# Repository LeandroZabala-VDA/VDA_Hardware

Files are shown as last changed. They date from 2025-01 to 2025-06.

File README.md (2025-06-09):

# VDA_Hardware

This repository contains the hardware design files for the **VDA Signal Acquisition System**, a device developed for the non-invasive measurement of **Arterial Diameter Variation (VDA)** using piezoelectric transducers. The system is intended for biomedical research applications and has been validated in both laboratory and clinical environments.

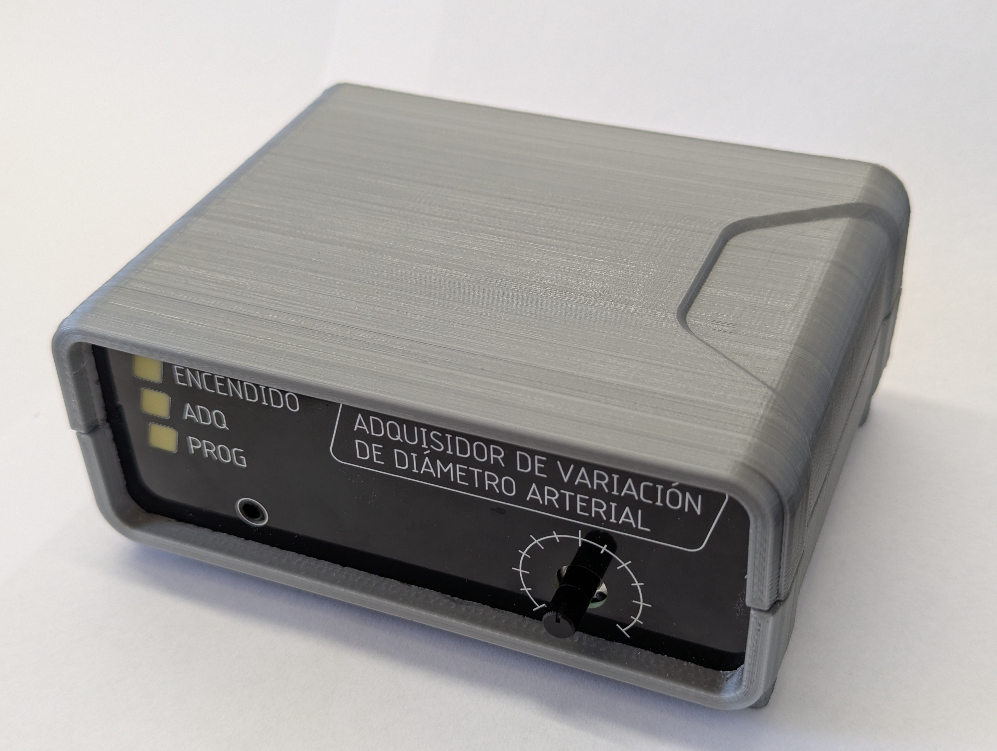
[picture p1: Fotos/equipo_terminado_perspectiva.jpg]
Equipo terminadp


## 📁 Repository Structure

- **/Adquisidor**  
  Contains all design files for the main acquisition board, including schematics, PCB layout, and bill of materials. This board handles signal conditioning, high-resolution analog-to-digital conversion, power regulation, and communication with the PC interface.

- **/frente del gabinete**  
  Includes the PCB designs used as front and rear panels for the device enclosure. These boards support mechanical mounting of connectors, status indicators, and user controls.

## 🛠️ Tools and Compatibility

- Designed using **Autodesk Eagle**  
- Compatible with Eagle version 9.6.2 or later

## ✅ Hardware Status

The version published here is fully functional and has been used in real experimental protocols and patient measurements. It is part of a broader open-source platform that includes firmware and a Python-based user interface.

Key features include:
- Support for a 27 mm piezoelectric transducer
- Fully differential charge amplifier
- Analog bandwidth: 0.16 Hz – 34 Hz
- 16-bit sigma-delta ADC
- 50 Hz digital notch filter
- Electrically isolated sensor interface

## 📂 Included Files

- `.sch` and `.brd` files (schematics and board layout)
- Bill of Materials (`.xls` / `.csv`)
- Reference images of the PCB and assembly
- Enclosure drawings or panel layouts (`.png`, `.step`, etc.)

## 📷 Preview

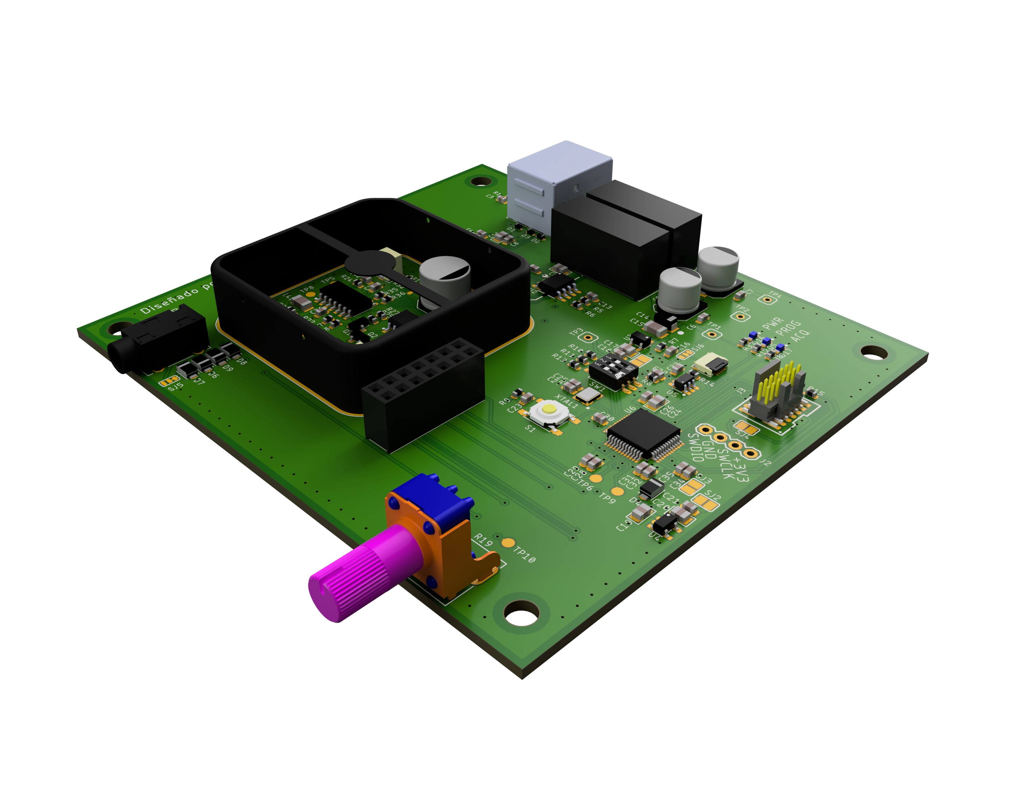
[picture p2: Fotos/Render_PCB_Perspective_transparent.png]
Render PCB


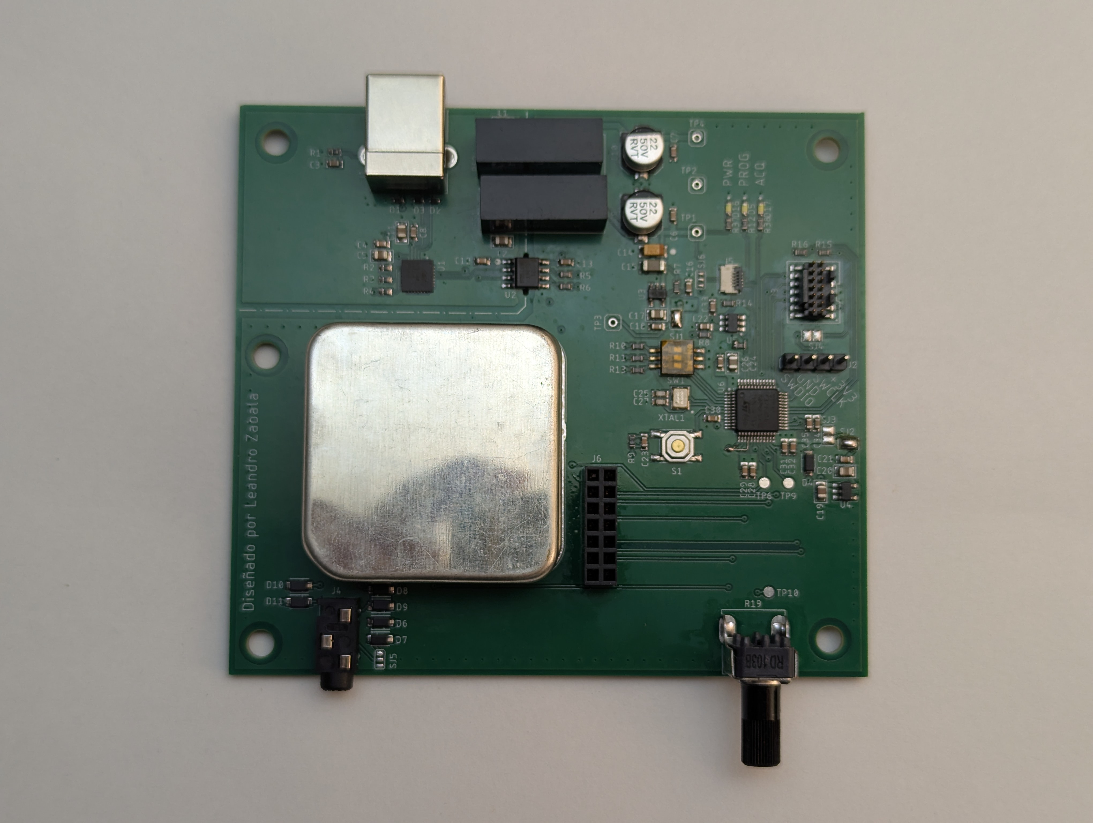
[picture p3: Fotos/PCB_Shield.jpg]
Real PCB


## 🧩 Related Work

This hardware was developed as part of a final project at the **Laboratorio de Bioingeniería (LABI)**, Universidad Nacional de Mar del Plata (Argentina), and was used in the context of scientific publications, including a peer-reviewed IEEE article.

## 🛡 License

All hardware design files in this repository are licensed under the **CERN Open Hardware License v2 - Strongly Reciprocal (CERN-OHL-S)**.

Any derivative work must also remain open and be shared under the same terms. 

## 📬 Contact

For questions, suggestions or collaboration, feel free to open an issue or contact me.

leandrozabala@mdp.edu.ar

---

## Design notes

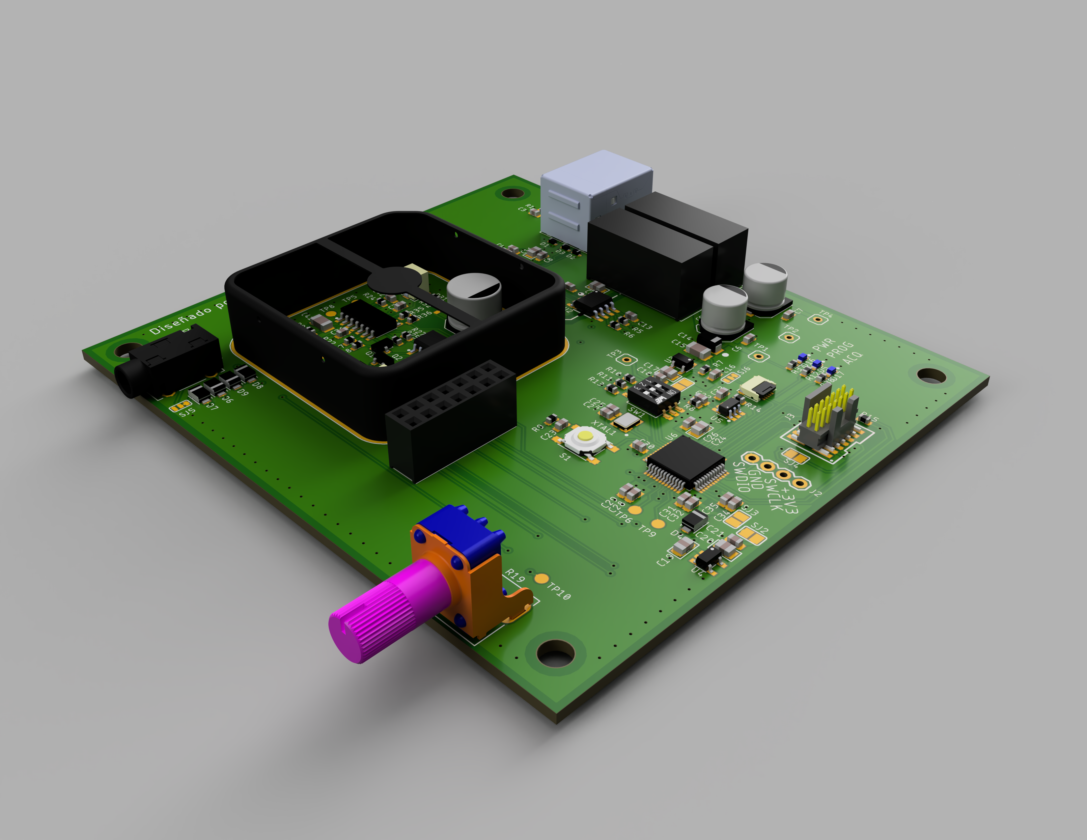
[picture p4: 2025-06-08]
Fotos/Render_PCB_Perspective_gray.png

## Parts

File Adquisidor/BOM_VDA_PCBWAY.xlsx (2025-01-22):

Item # | Parts | Qty | MPN | Description | Package | Instruction | LINK
1 | R5, R6, R15, R16, R29, R33,R20, R21 | 8 | RC0603FR-07100RL |  | R_0603 |  | https://www.lcsc.com/product-detail/Chip-Resistor-Surface-Mount_YAGEO-RC0603FR-07100RL_C105588.html
2 | R7, R24 | 2 | RC0603FR-07100KL |  | R_0603 |  | https://www.lcsc.com/product-detail/Chip-Resistor-Surface-Mount_YAGEO-RC0603FR-07100KL_C14675.html
3 | R22, R23 | 2 | CRCW060310M0DHEAP |  | R_0603 |  | https://www.lcsc.com/product-detail/Chip-Resistor-Surface-Mount_Vishay-Intertech-CRCW060310M0DHEAP_C4098828.html
4 | R8, R9, R10, R11, R13, R14 | 6 | RC0603FR-0710KL |  | R_0603 |  | https://www.lcsc.com/product-detail/Chip-Resistor-Surface-Mount_YAGEO-RC0603FR-0710KL_C98220.html
5 | R26 | 1 | RC0603FR-07150RL |  | R_0603 |  | https://www.lcsc.com/product-detail/Chip-Resistor-Surface-Mount_YAGEO-RC0603FR-07150RL_C114608.html
6 | R18 | 1 | RC0603FR-0733KL |  | R_0603 |  | https://www.lcsc.com/product-detail/Chip-Resistor-Surface-Mount_YAGEO-RC0603FR-0733KL_C126359.html
7 | R25, R28, R31, R35 | 4 | RC0603FR-071KL |  | R_0603 |  | https://www.lcsc.com/product-detail/Chip-Resistor-Surface-Mount_YAGEO-RC0603FR-071KL_C22548.html
8 | R36 | 1 | RC0603FR-072K2L |  | R_0603 |  | https://www.lcsc.com/product-detail/Chip-Resistor-Surface-Mount_YAGEO-RC0603FR-072K2L_C114662.html
9 | R12, R37, R38 | 3 | RC0603FR-07270RL |  | R_0603 |  | https://www.lcsc.com/product-detail/Chip-Resistor-Surface-Mount_YAGEO-RC0603FR-07270RL_C137754.html
10 | R27 | 1 | RC0603FR-072KL |  | R_0603 |  | https://www.lcsc.com/product-detail/Chip-Resistor-Surface-Mount_YAGEO-RC0603FR-072KL_C105576.html
11 | R4 | 1 | RC0402FR-071KL |  | R0402 |  | https://www.lcsc.com/product-detail/Chip-Resistor-Surface-Mount_YAGEO-RC0402FR-071KL_C106235.html
12 | R2 | 1 | RC0402FR-0722K1L |  | R0402 |  | https://lcsc.com/product-detail/Chip-Resistor-Surface-Mount_YAGEO-RC0402FR-0722K1L_C163478.html
13 | R1, R3 | 2 | RC0402FR-0747K5L |  | R0402 |  | https://lcsc.com/product-detail/Chip-Resistor-Surface-Mount_YAGEO-RC0402FR-0747K5L_C137974.html
14 | R30, R32 | 2 | 3224W-1-501E |  | RV3.2X4 |  | https://www.lcsc.com/product-detail/Potentiometers-Variable-Resistors_BOURNS-3224W-1-501E_C116324.html?s_z=n_3224W
15 | R19 | 1 | RK09K1110077 |  | POT-09VR1M |  | https://www.lcsc.com/product-detail/Potentiometers-Variable-Resistors_ALPSALPINE-RK09K1110077_C3020620.html?s_z=n_RK09K1110077
16 | R17, R34 | 2 | DNP |  | R_0603
17 | C3, C4, C6, C7, C8, C12, C13, C23, C26, C28, C29, C30, C31, C32, C33, C36, C37, C38, C39,C18, C21, C35 | 22 | C0603C104K5RACAUTO |  | C_0603 |  | https://lcsc.com/product-detail/Multilayer-Ceramic-Capacitors-MLCC-SMD-SMT_KEMET-C0603C104K5RACAUTO_C129621.html
18 | C40, C41 | 2 | GRM31C5C1H104FA01L | NP0 | C_1206 |  | https://www.lcsc.com/product-detail/Multilayer-Ceramic-Capacitors-MLCC-SMD-SMT_Murata-Electronics-GRM31C5C1H104FA01L_C2981728.html?s_z=n_C0G
19 | C25, C27 | 2 | CC0603JRNPO9BN100 |  | C_0603 |  | https://www.lcsc.com/product-detail/Multilayer-Ceramic-Capacitors-MLCC-SMD-SMT_YAGEO-CC0603JRNPO9BN100_C106245.html
20 | C16, C22 | 2 | CL10B224KA8NNNC |  | C_0603 |  | https://www.lcsc.com/product-detail/Multilayer-Ceramic-Capacitors-MLCC-SMD-SMT_Samsung-Electro-Mechanics-CL10B224KA8NNNC_C21120.html
21 | C42 | 1 | CC0603JRX7R9BB473 |  | C_0603 |  | https://www.lcsc.com/product-detail/Multilayer-Ceramic-Capacitors-MLCC-SMD-SMT_YAGEO-CC0603JRX7R9BB473_C519554.html
22 | C34 | 1 | CL10A105KO8NNNC |  | C_0603 |  | https://lcsc.com/product-detail/Multilayer-Ceramic-Capacitors-MLCC-SMD-SMT_Samsung-Electro-Mechanics-CL10A105KO8NNNC_C1592.html
23 | C5, C11,C24,C1, C2, C17, C20 | 7 | CL21A475KAQNNNE |  | C_0805 |  | https://www.lcsc.com/product-detail/Multilayer-Ceramic-Capacitors-MLCC-SMD-SMT_Samsung-Electro-Mechanics-CL21A475KAQNNNE_C1779.html
24 | C19 | 1 | CL21A106KAYNNNE |  | C_0805 |  | https://www.lcsc.com/product-detail/Multilayer-Ceramic-Capacitors-MLCC-SMD-SMT_Samsung-Electro-Mechanics-CL21A106KAYNNNE_C15850.html
25 | C15 | 1 | HGC1206R5476M250NSPJ |  | C_1206 |  | https://www.lcsc.com/product-detail/Multilayer-Ceramic-Capacitors-MLCC-SMD-SMT_Chinocera-HGC1206R5476M250NSPJ_C22367835.html
26 | C14 | 1 | TAJA476K006RNJ |  | A_3216 |  | https://lcsc.com/product-detail/Tantalum-Capacitors_Kyocera-AVX-TAJA476K006RNJ_C7190.html
27 | C9, C10 | 2 | RVT1H220M0605 |  | CAPAE660X590N |  | https://www.lcsc.com/product-detail/Aluminum-Electrolytic-Capacitors-SMD_ROQANG-RVT1H220M0605_C72505.html
28 | C43 | 1 |  |  | CAPAE830X680N
29 | D1, D2, D3 | 3 | LESD5D5.0CT1G |  | SOD523 |  | https://www.lcsc.com/product-detail/span-style-background-color-ff0-ESD-span-and-Surge-Protection-TVS-span-style-background-color-ff0-ESD-span_UMW-Youtai-Semi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
30 | D4 | 1 | LMBR140T1G |  | SOD123W |  | https://www.lcsc.com/product-detail/Schottky-Diodes_LRC-LMBR140T1G_C81142.html
31 | D16, D5, D17 | 3 | XL-1608UWC-04 |  | LED_0603_ARROW |  | https://www.lcsc.com/product-detail/LED-Indication-Discrete_XINGLIGHT-XL-1608UWC-04_C965808.html
32 | D6, D7, D8, D9, D10, D11, D12, D13, D14, D15 | 10 | 1N4148W |  | SOD123W |  | https://www.lcsc.com/product-detail/Switching-Diode_Jiangsu-Changjing-Electronics-Technology-Co-Ltd-1N4148W_C2099.html
33 | U1 | 1 | CP2102N-A02-GQFN28R |  | MLP28 |  | https://lcsc.com/product-detail/USB-ICs_SILICON-LABS-CP2102N-A02-GQFN28R_C964632.html
34 | U2 | 1 | ISO7721DR |  | SO8 |  | https://www.lcsc.com/product-detail/Digital-Isolators_Texas-Instruments-ISO7721DR_C366164.html?s_z=n_ISO7721DR
35 | U3, U4 | 2 | LP5907MFX-3.3/NOPB |  | SOT23-5 |  | https://www.lcsc.com/product-detail/Voltage-Regulators-Linear-Low-Drop-Out-LDO-Regulators_Texas-Instruments-LP5907MFX-3-3-NOPB_C80670.html
36 | U5 | 1 | SN74LVC1G175DBVR |  | SOT-23-6 |  | https://www.lcsc.com/product-detail/Flip-Flops_Texas-Instruments-SN74LVC1G175DBVR_C128412.html?s_z=n_SN74LVC1G175
37 | U6 | 1 | STM32F373CBT6 |  | QFP50P900X900X160-48N |  | https://www.lcsc.com/product-detail/Microcontrollers-MCU-MPU-SOC_STMicroelectronics-STM32F373CBT6_C1337334.html
38 | U7 | 1 | TL074IDT |  | SOIC127P600X175-14N |  | https://www.lcsc.com/product-detail/FET-Input-Amplifiers_STMicroelectronics-TL074IDT_C107644.html?s_z=n_TL074
39 | U8 | 1 | LM13700M/NOPB |  | SO16 |  | https://www.lcsc.com/product-detail/Operational-Amplifier_Texas-Instruments-LM13700M-NOPB_C1346265.html?s_z=n_LM13700
40 | Q1, Q2 | 2 | BC856B,215 |  | SOT-23 |  | https://www.lcsc.com/product-detail/Bipolar-BJT_Nexperia-BC856B-215_C109310.html?s_z=n_BC856
41 | PS1, PS2 | 2 | IF0505S-2W |  | 0505S-2WR3 |  | https://www.lcsc.com/product-detail/Isolated-Power-Modules_YLPTEC-IF0505S-2W_C5369639.html?s_z=n_F0505S-2W
42 | SW1 | 1 | DSHP03TSGER |  | DIPSW-3 |  | https://www.lcsc.com/product-detail/DIP-Switches_kangshen-DSHP03TSGER_C3293143.html
43 | SHIELD1 | 1 | MS384-10F |  | MS384 | Only solder 2 pads. DO NOT SOLDER ALL THE WAY ARROUND TO THE GND PLANE | https://www.digikey.com/en/products/detail/masach-tech-ltd/MS384-10F/12084532
44 | SHIELD_COVER | 1 | MS384-10C |  |  | Placed on top of the shield | https://www.digikey.com/en/products/detail/masach-tech-ltd/MS384-10C/12084599
45 | S1 | 1 | TS-1187A-B-A-B |  | SMTR2 |  | https://www.lcsc.com/product-detail/Tactile-Switches_XKB-Connection-TS-1187A-B-A-B_C318884.html
46
47 | J1 | 1 | BF 90° |  | USB-B |  | https://www.lcsc.com/product-detail/USB-Connectors_SHOU-HAN-BF-90_C456014.html
48 | J2 | 1 | PZ254V-11-04P |  | 1X04 |  | https://www.lcsc.com/product-detail/Pin-Headers_XFCN-PZ254V-11-04P_C2691448.html
49 | J3 | 1 | FTSH-107-01-L-DV-K-A |  | SAMTEC_FTSH-107-01-L-DV-K-A |  | https://www.lcsc.com/product-detail/Pin-Headers_Samtec-FTSH-107-01-L-DV-K-A_C5563894.html?s_z=n_FTSH-107-01-L-DV-K-A
50 | J4 | 1 | PJ-3200 |  | PJ-3200 |  | https://www.lcsc.com/product-detail/Audio-Connectors_XKB-Connection-PJ-3200_C2689690.html?s_z=n_PJ-3200
51 | J5 | 1 | F0504-H-05-10G-R | FFC, FPC (Flat Flexible) Connector | F0504-H-05-10G-R |  | https://www.lcsc.com/product-detail/FFC-FPC-Flat-Flexible-Connector-Assemblies_XFCN-F0504-H-05-10G-R_C2889992.html?s_z=n_F0504-H-05-10G-R
52 | J6 | 1 | 2.54-2*7P |  | CONN-VERT-2.54MM-2X7-FEMALE |  | https://www.lcsc.com/product-detail/Female-Headers_BOOMELE-Boom-Precision-Elec-2-54-2-7P_C38844.html
53 | XTAL1 | 1 | S32080001010500 |  | XTAL3.2X2.5 |  | https://lcsc.com/product-detail/Crystals_JGHC-S32080001010500_C479191.html
54 | FLEX | 1 | JS05A-05P-120-4-8 |  | Flex 12cm 5P pitch=0.5mm | Connected to J5 | https://www.lcsc.com/product-detail/FFC-Cable-Flexible-Flat-Cable_JUSHUO-JS05A-05P-120-4-8_C5371200.html

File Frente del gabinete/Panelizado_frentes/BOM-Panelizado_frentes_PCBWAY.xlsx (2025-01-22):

Item # | Parts | Qty | MPN | Description | Package | Instruction | LINK
1 | R2, R5, R8 | 3 | RC0603FR-07100KL |  | R_0603 |  | https://www.lcsc.com/product-detail/Chip-Resistor-Surface-Mount_YAGEO-RC0603FR-07100KL_C14675.html
2 | R1, R3, R4, R6, R7, R9 | 6 | RC0603FR-07100RL |  | R_0603 |  | https://www.lcsc.com/product-detail/Chip-Resistor-Surface-Mount_YAGEO-RC0603FR-07100RL_C105588.html
3 | Q2, Q3, Q1 | 3 | BSS138 |  | SOT-23 |  | https://www.lcsc.com/product-detail/MOSFETs_MDD-Microdiode-Semiconductor-BSS138_C427380.html
4 | J1 | 1 | F0504-H-05-10G-R | FFC, FPC (Flat Flexible) Connector | F0504-H-05-10G-R |  | https://www.lcsc.com/product-detail/FFC-FPC-Flat-Flexible-Connector-Assemblies_XFCN-F0504-H-05-10G-R_C2889992.html?s_z=n_F0504-H-05
5 | D4, D5, D6 | 3 | VLRK31R1S2-GS08 |  | VLRK31 |  | https://www.lcsc.com/product-detail/LED-Indication-Discrete_Vishay-Intertech-VLRK31R1S2-GS08_C5346037.html?s_z=n_VLRK31
6 | FLEX | 1 | YTC05B-05P-220-3-4 | Connected to J1 | Flex 22cm 5P pitch=0.5mm | Connected to J1 | https://www.lcsc.com/product-detail/FFC-Cable-Flexible-Flat-Cable_YIYUAN-YTC05B-05P-220-3-4_C20069054.html

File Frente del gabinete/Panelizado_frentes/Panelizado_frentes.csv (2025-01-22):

Qty | Value | Device | Package | Parts | Description | MPN | LINK
3 | 100K | R_0603 | R_0603 | R2, R5, R8 |  | RC0603FR-07100KL | https://www.lcsc.com/product-detail/Chip-Resistor-Surface-Mount_YAGEO-RC0603FR-07100KL_C14675.html
6 | 100R | R_0603 | R_0603 | R1, R3, R4, R6, R7, R9 |  | RC0603FR-07100RL | https://www.lcsc.com/product-detail/Chip-Resistor-Surface-Mount_YAGEO-RC0603FR-07100RL_C105588.html
3 | BSS138 | N-MOS_SOT23-3 | SOT-23 | 2, 3, Q1 |  | BSS138 | https://www.lcsc.com/product-detail/MOSFETs_MDD-Microdiode-Semiconductor-BSS138_C427380.html
1 | F0504-H-05-10G-R | F0504-H-05-10G-R | F0504-H-05-10G-R | J1 | FFC, FPC (Flat Flexible) Connector | F0504-H-05-10G-R | https://www.lcsc.com/product-detail/FFC-FPC-Flat-Flexible-Connector-Assemblies_XFCN-F0504-H-05-10G-R_C2889992.html?s_z=n_F0504-H-05
3 | LED-REVERSE_MOUNT | LED-REVERSE_MOUNT | VLRK31 | D4, D5, D6 |  | VLRK31R1S2-GS08 | https://www.lcsc.com/product-detail/LED-Indication-Discrete_Vishay-Intertech-VLRK31R1S2-GS08_C5346037.html?s_z=n_VLRK31

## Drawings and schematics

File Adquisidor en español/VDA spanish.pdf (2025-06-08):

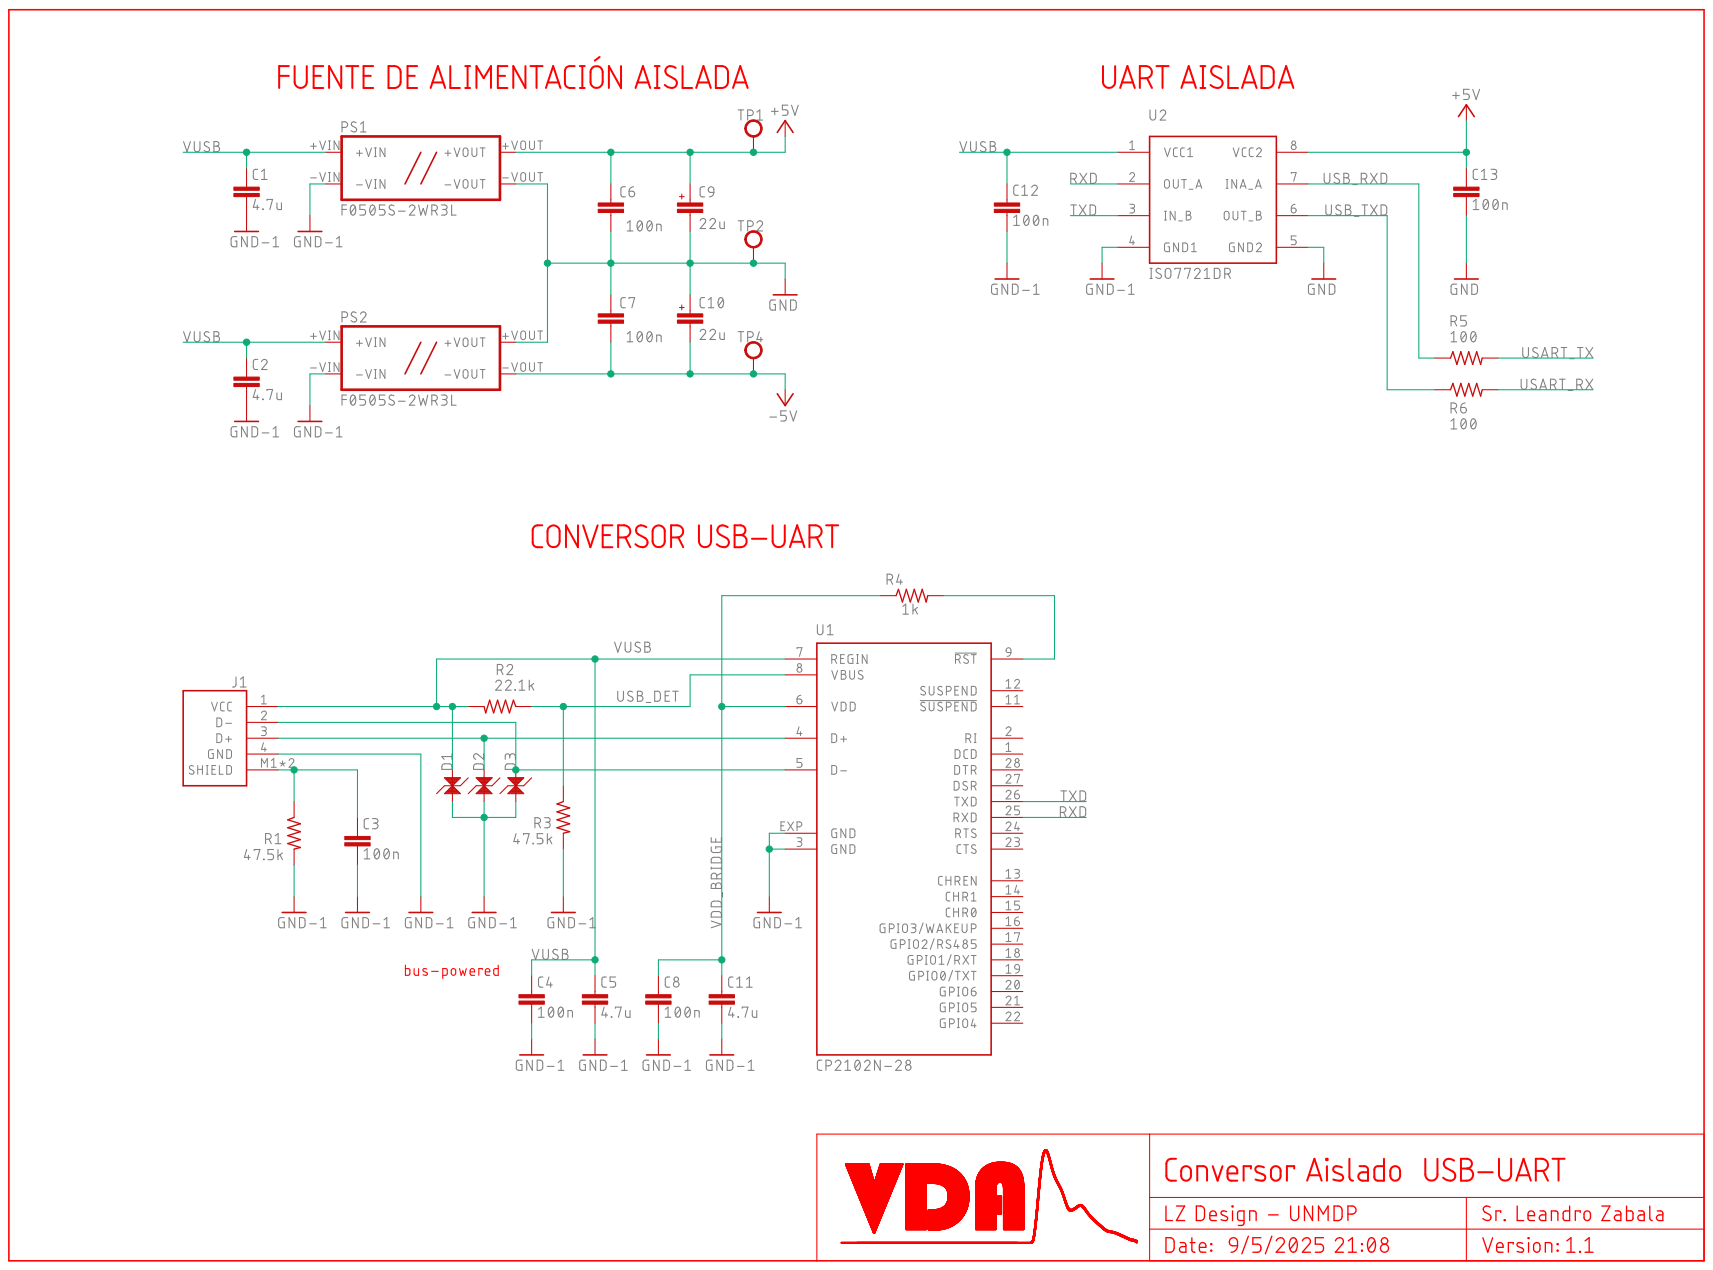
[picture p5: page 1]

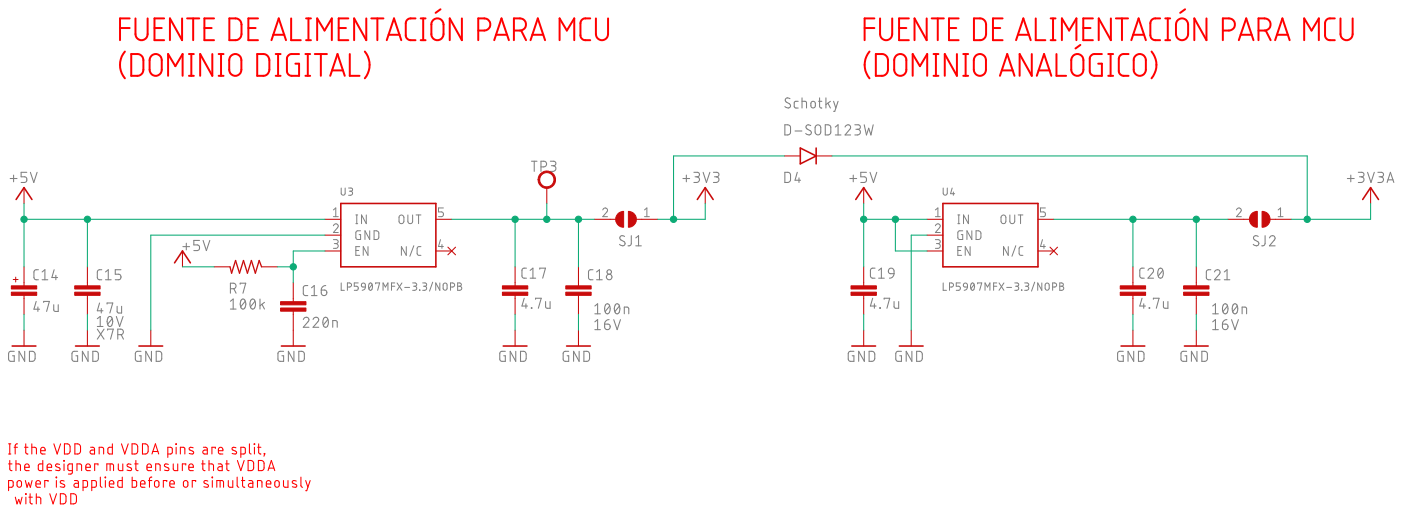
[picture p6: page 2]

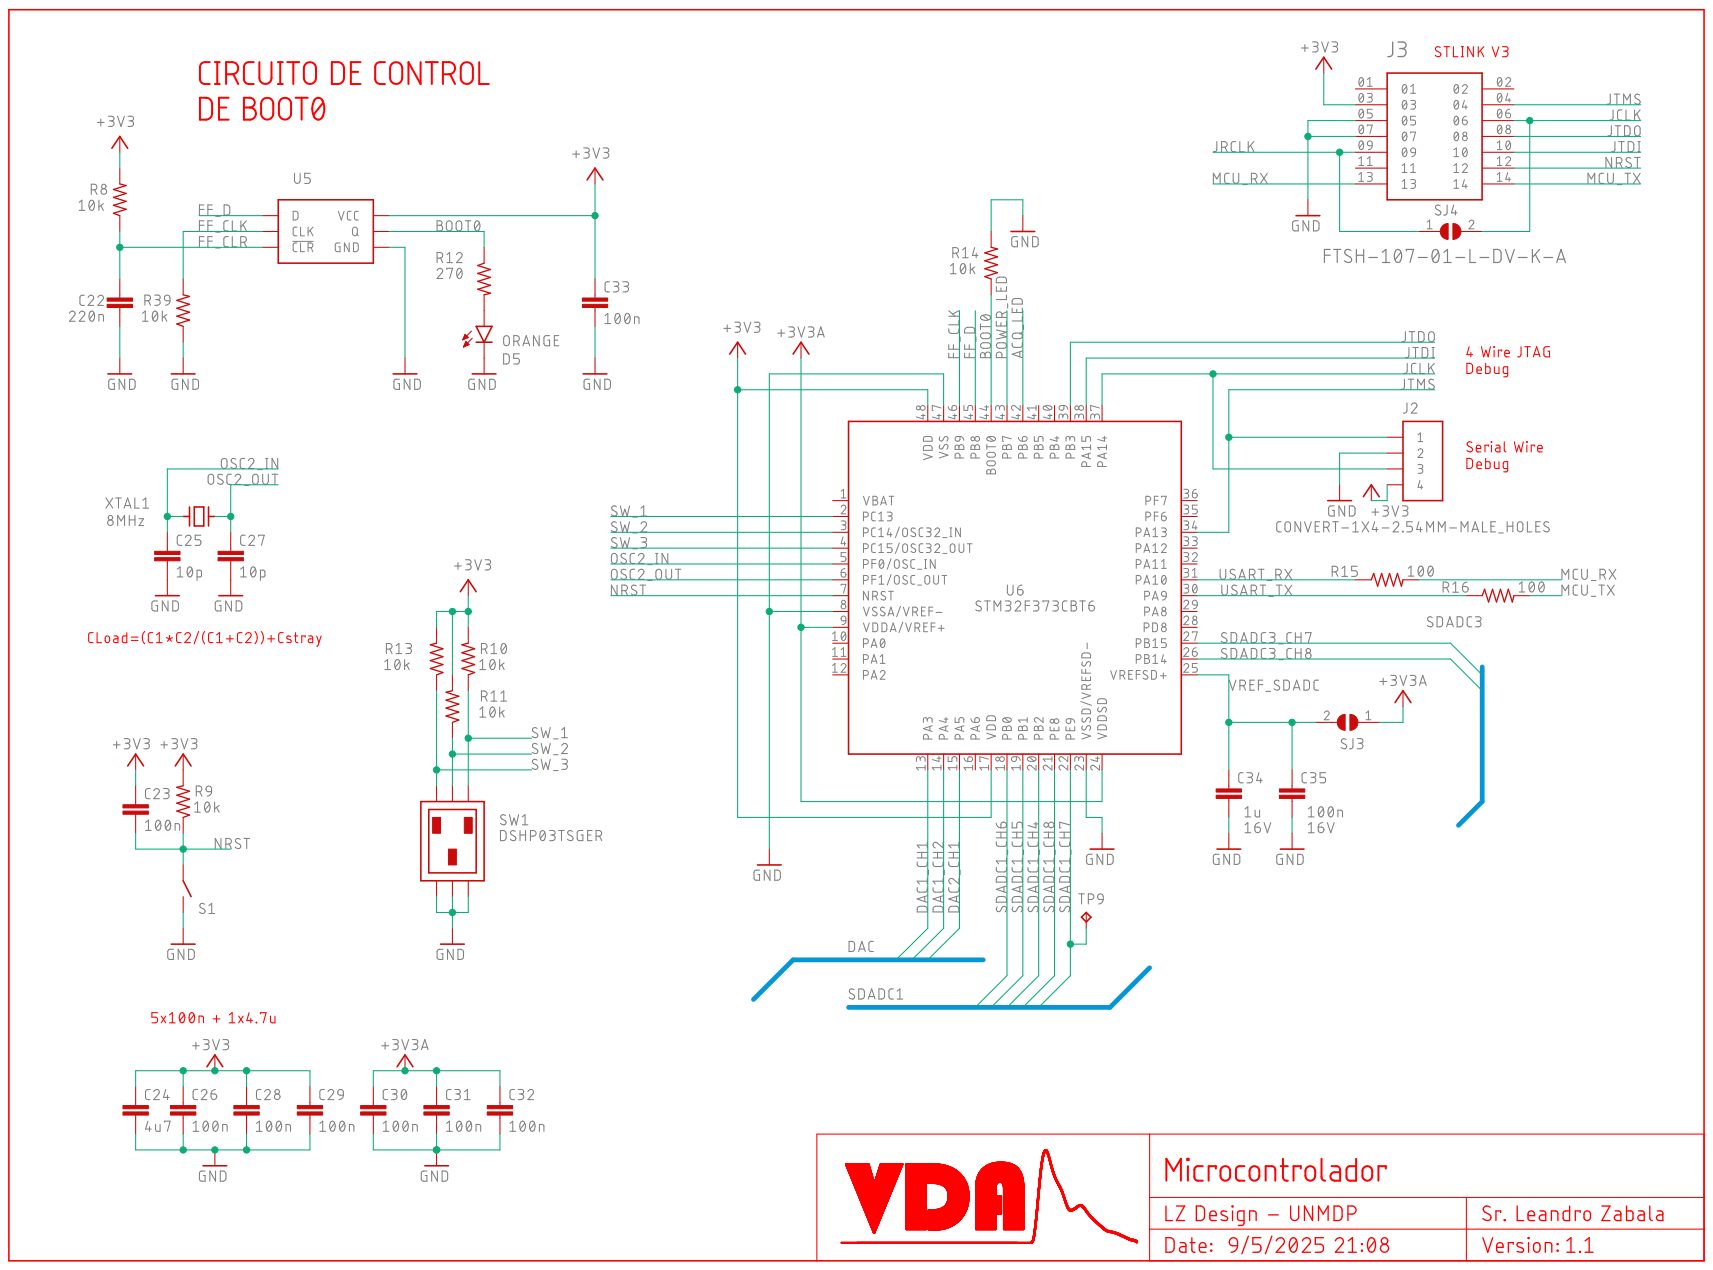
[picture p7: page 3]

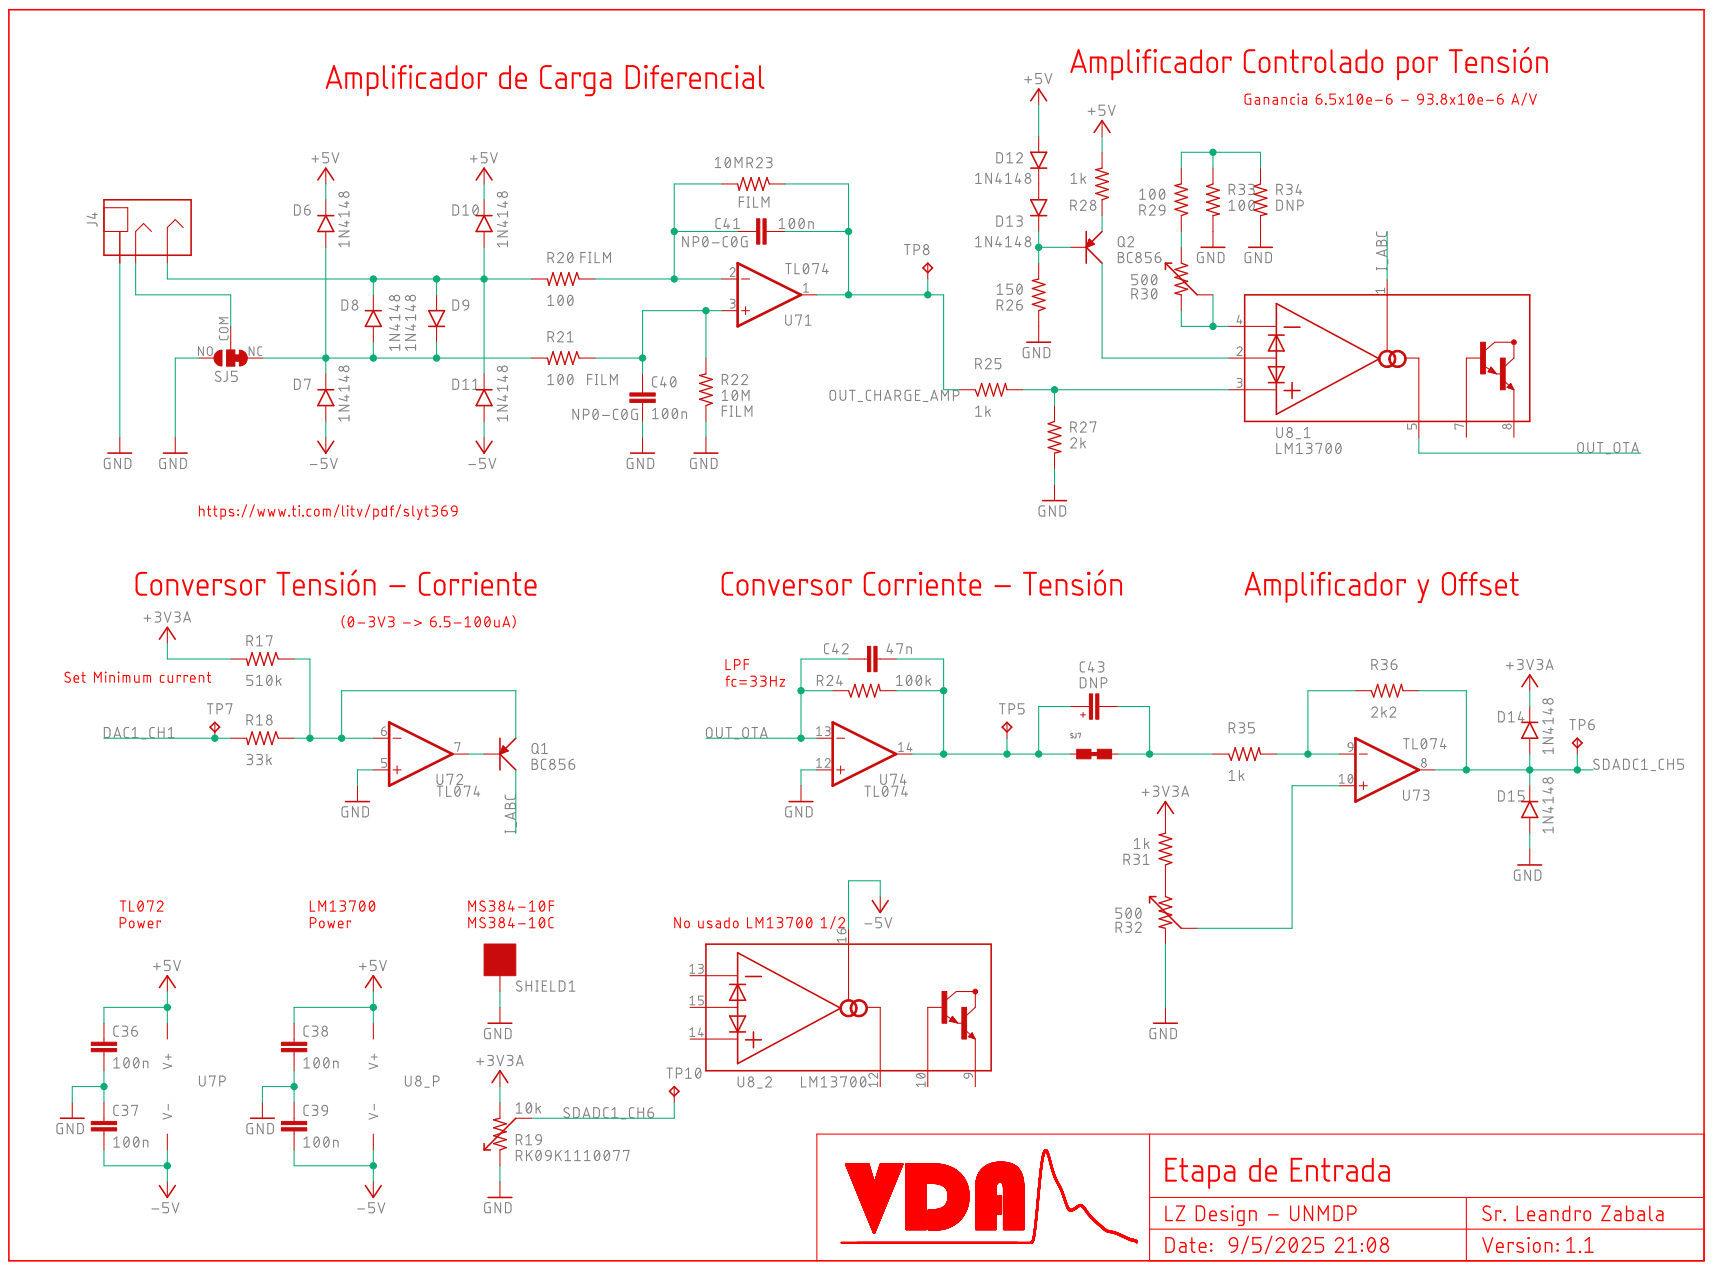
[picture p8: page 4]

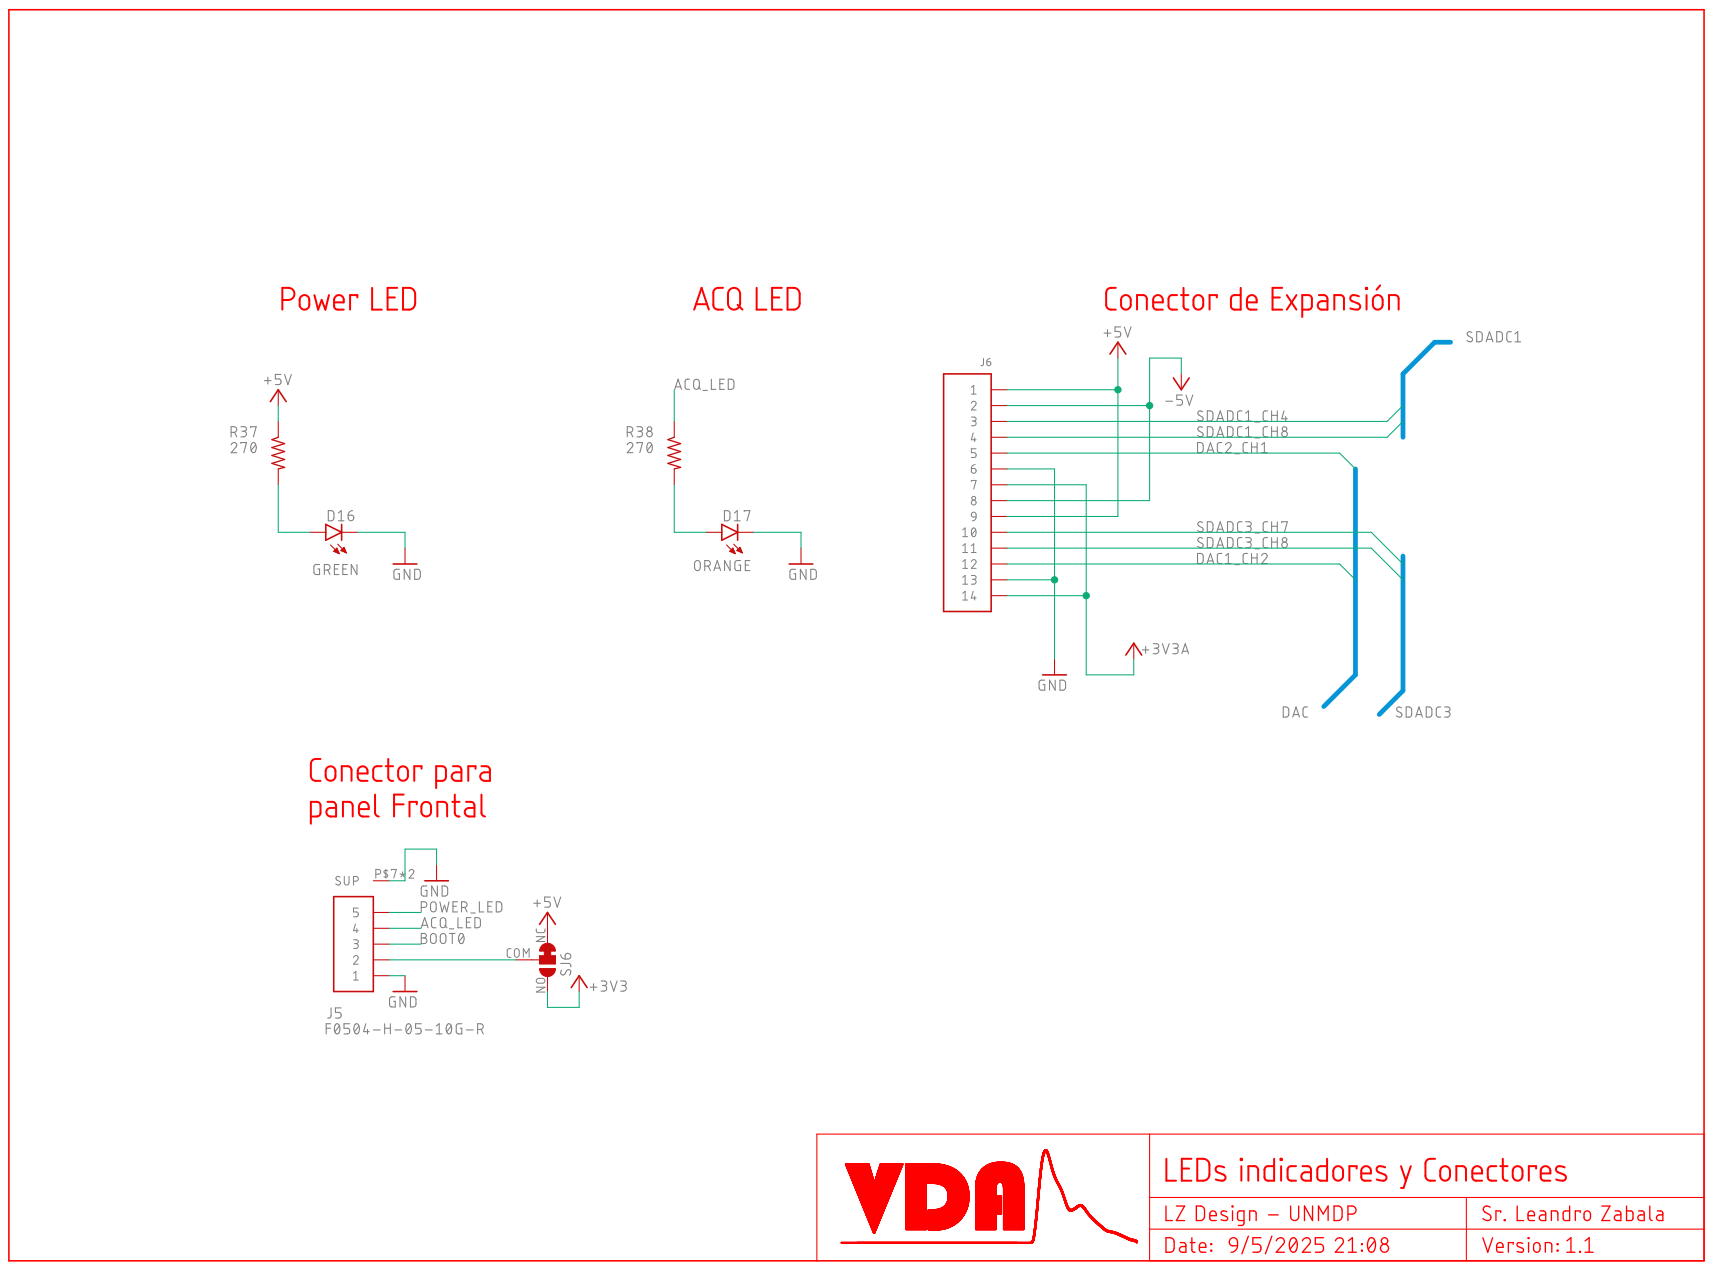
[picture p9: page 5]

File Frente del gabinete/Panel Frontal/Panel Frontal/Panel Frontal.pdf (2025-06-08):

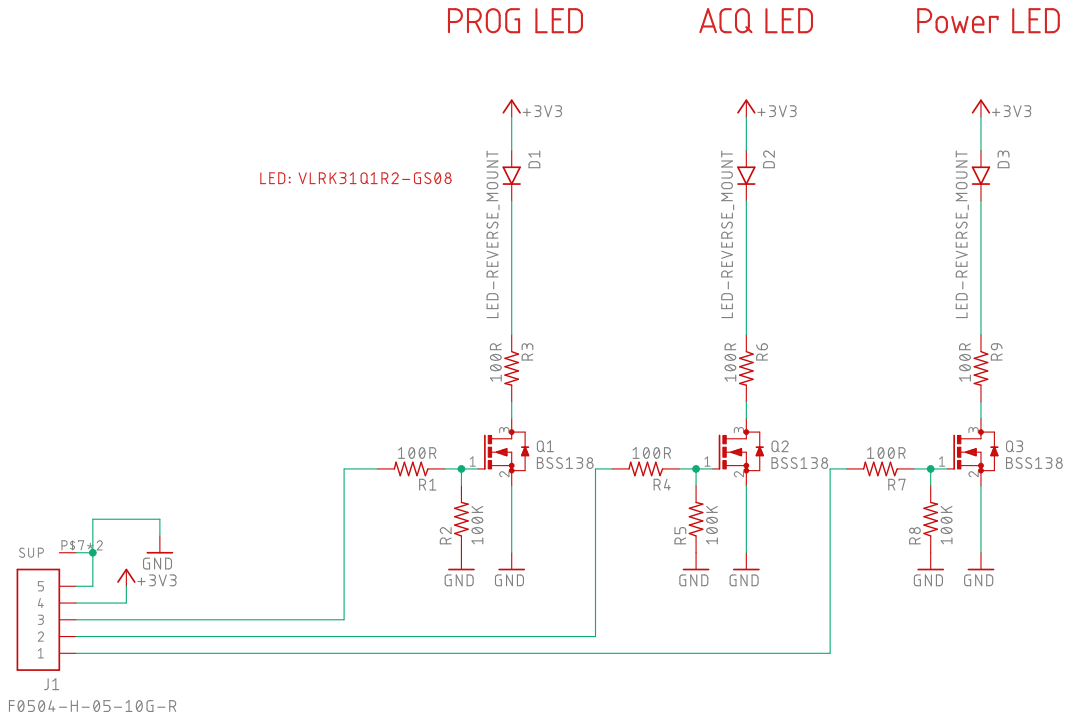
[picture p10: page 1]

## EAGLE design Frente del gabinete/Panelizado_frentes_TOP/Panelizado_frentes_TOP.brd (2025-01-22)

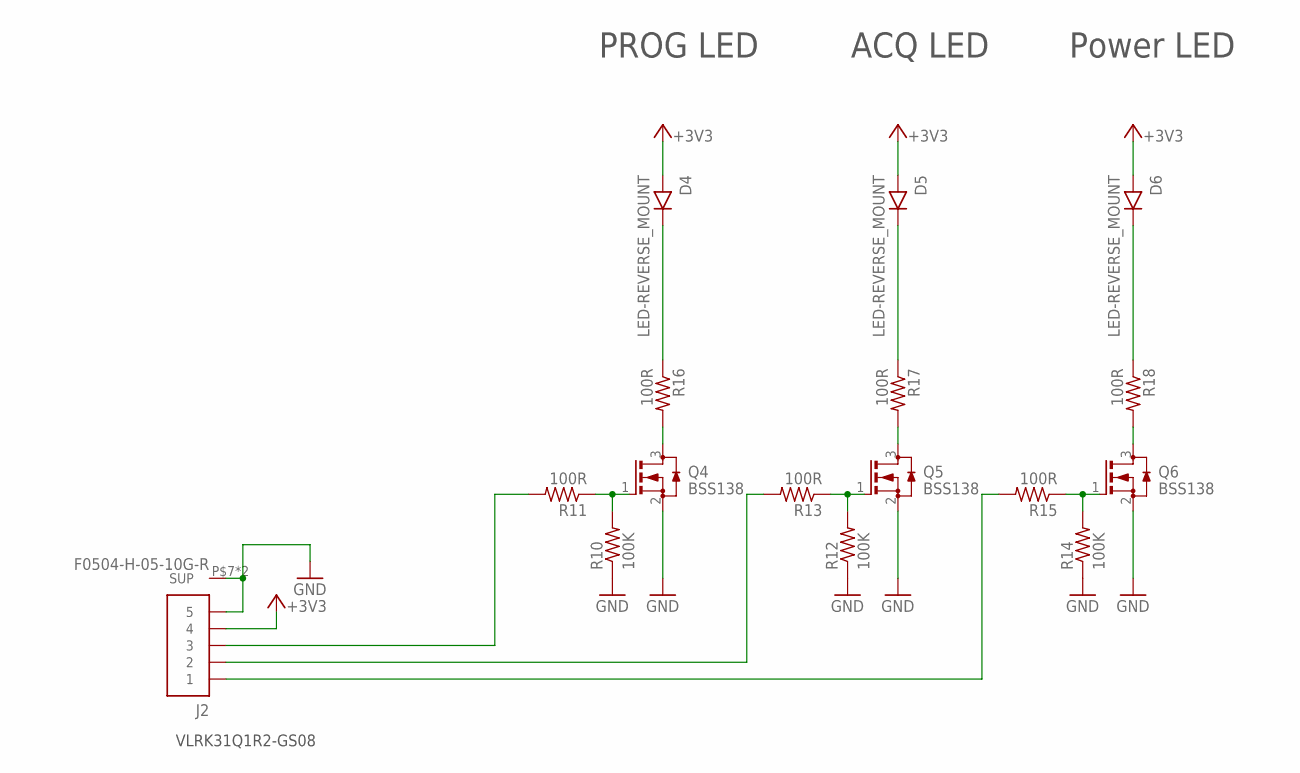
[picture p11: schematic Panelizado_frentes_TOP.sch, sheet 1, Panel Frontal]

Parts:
D4, D5, D6: LED-REVERSE_MOUNT; VLRK31
J2: F0504-H-05-10G-R
Q4, Q5, Q6: BSS138; SOT-23
R10, R12, R14: 100K; R_0603
R11, R13, R15, R16, R17, R18: 100R; R_0603

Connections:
+3V3: D4.A, D5.A, D6.A, J2.P$4 (4)
GND: J2.P$5 (5), J2.P$7 (SUP), J2.P$8 (SUP), Q4.2 (S), Q5.2 (S), Q6.2 (S), R10.1, R12.1, R14.1
unnamed: Q4.1 (G), R10.2, R11.1
unnamed: Q5.1 (G), R12.2, R13.1
unnamed: Q6.1 (G), R14.2, R15.1
unnamed: J2.P$3 (3), R11.2
unnamed: J2.P$2 (2), R13.2
unnamed: J2.P$1 (1), R15.2
unnamed: D4.K, R16.1
unnamed: Q4.3 (D), R16.2
unnamed: D5.K, R17.1
unnamed: Q5.3 (D), R17.2
unnamed: D6.K, R18.1
unnamed: Q6.3 (D), R18.2

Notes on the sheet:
VLRK31Q1R2-GS08
Power LED
ACQ LED
PROG LED

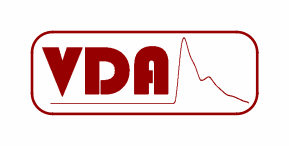
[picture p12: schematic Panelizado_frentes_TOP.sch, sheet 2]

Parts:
U$1: LOGO_VDA-3CM

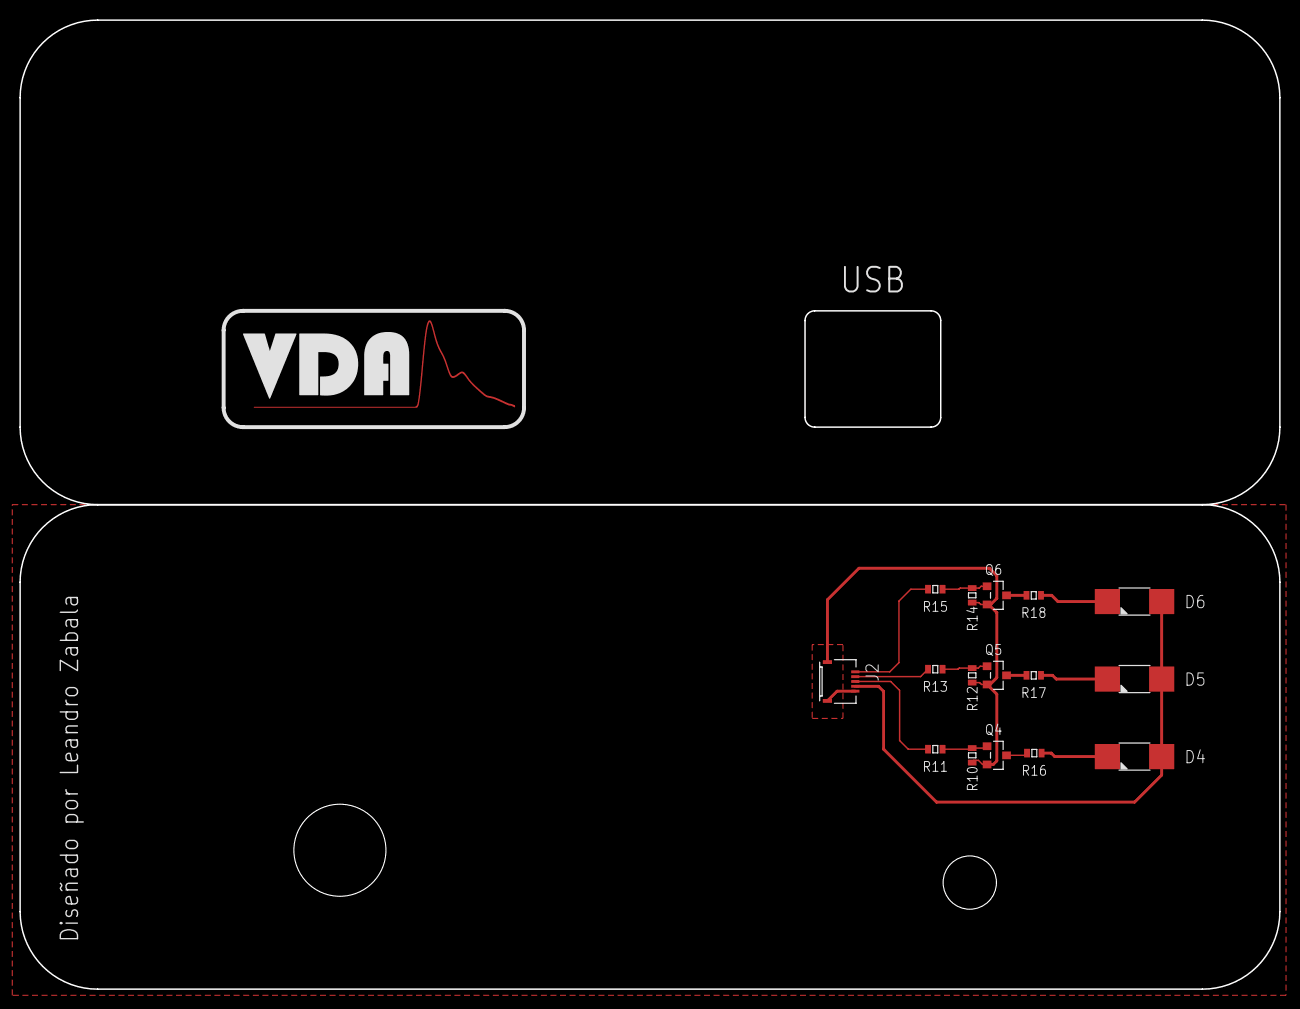
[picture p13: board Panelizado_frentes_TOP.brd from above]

Board: 2 copper layers, 130.0 x 100.0 mm, 17 parts (0 on the bottom side), 14 nets.

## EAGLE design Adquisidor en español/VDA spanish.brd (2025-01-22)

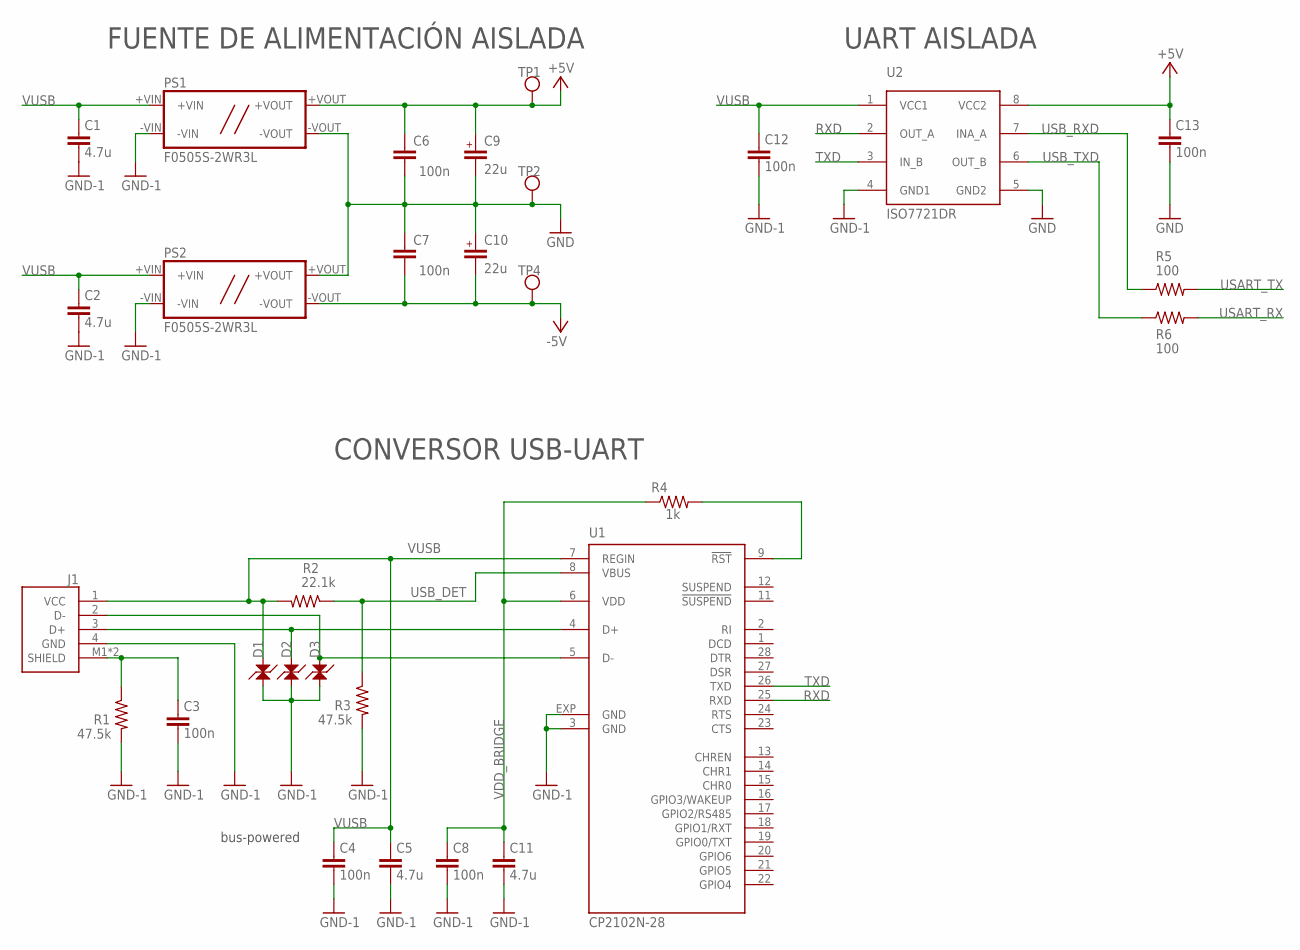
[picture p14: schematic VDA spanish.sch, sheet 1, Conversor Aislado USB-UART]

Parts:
C1, C2, C5, C11: 4.7u; C_0805
C3, C4, C6, C7, C8, C12, C13: 100n; C_0603
C9, C10: 22u; CAPAE660X590N
D1, D2, D3: LESD5D5.0CT1G; SOD523
J1: USB-2.0; USB-B
PS1, PS2: F0505S-2WR3L; 0505S-2WR3
R1, R3: 47.5k; R0402
R2: 22.1k; R0402
R4: 1k; R0402
R5, R6: 100; R_0603
TP1, TP2, TP4: HOLE_0.8MM
U1: CP2102N-28; MLP28
U2: ISO7721DR; SO8

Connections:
+5V: C6.P$1 (1), C9.+, C13.P$1 (1), PS1.+VOUT, TP1.1, U2.8 (VCC2); also elsewhere on the board
-5V: C7.P$2 (2), C10.-, PS2.-VOUT, TP4.1; also elsewhere on the board
GND: C6.P$2 (2), C7.P$1 (1), C9.-, C10.+, C13.P$2 (2), PS1.-VOUT, PS2.+VOUT, TP2.1, U2.5 (GND2); also elsewhere on the board
GND-1: C1.P$2 (2), C2.P$2 (2), C3.P$2 (2), C4.P$2 (2), C5.P$2 (2), C8.P$2 (2), C11.P$2 (2), C12.P$2 (2), D1.C, D2.C, D3.C, J1.4 (GND), PS1.-VIN, PS2.-VIN, R1.2, R3.2, U1.3 (GND), U1.EXP (GND), U2.4 (GND1)
unnamed: R4.2, U1.9 (!RST)
RXD: U1.25 (RXD), U2.2 (OUT_A)
SHIELD: C3.P$1 (1), J1.M1 (SHIELD), J1.M2 (SHIELD), R1.1
TXD: U1.26 (TXD), U2.3 (IN_B)
USART_RX: R6.2; also elsewhere on the board
USART_TX: R5.2; also elsewhere on the board
USB_DET: R2.1, R3.1, U1.8 (VBUS)
USB_DN: D3.A, J1.2 (D-), U1.5 (D-)
USB_DP: D2.A, J1.3 (D+), U1.4 (D+)
USB_RXD: R5.1, U2.7 (INA_A)
USB_TXD: R6.1, U2.6 (OUT_B)
VDD_BRIDGE: C8.P$1 (1), C11.P$1 (1), R4.1, U1.6 (VDD)
VUSB: C1.P$1 (1), C2.P$1 (1), C4.P$1 (1), C5.P$1 (1), C12.P$1 (1), D1.A, J1.1 (VCC), PS1.+VIN, PS2.+VIN, R2.2, U1.7 (REGIN), U2.1 (VCC1)

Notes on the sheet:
CONVERSOR USB-UART
bus-powered
FUENTE DE ALIMENTACIÓN AISLADA
UART AISLADA

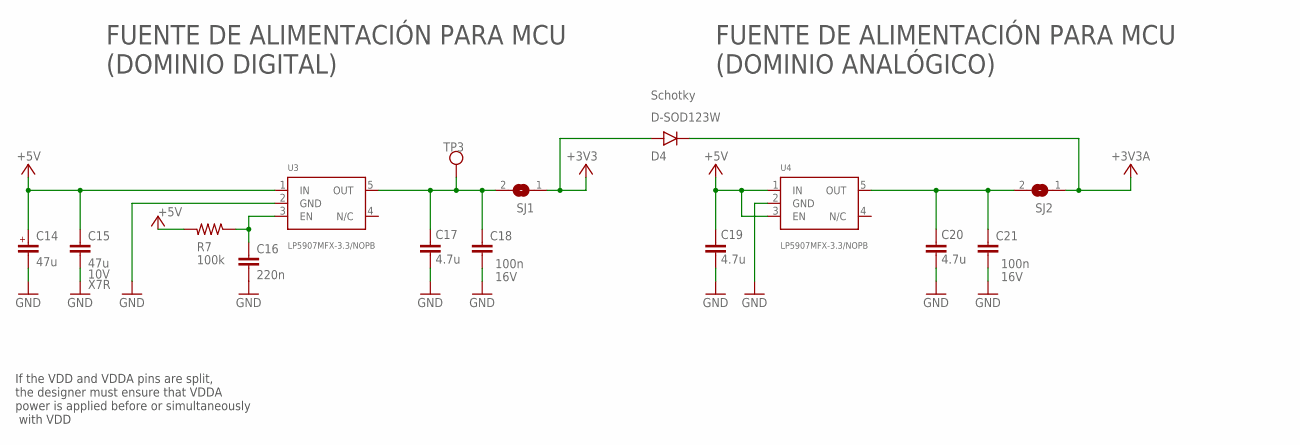
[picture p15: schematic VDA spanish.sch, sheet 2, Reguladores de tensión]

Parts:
C14: 47u; A_3216
C15: 47u; C_1206
C16: 220n; C_0603
C17, C19, C20: 4.7u; C_0805
C18, C21: 100n; C_0603
D4: D-SOD123W; SOD123W
R7: 100k; R_0603
SJ1, SJ2: SJ
TP3: HOLE_0.8MM
U3, U4: LP5907MFX-3.3/NOPB; SOT23-5

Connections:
+3V3: D4.A, SJ1.1; also elsewhere on the board
+3V3A: D4.C (K), SJ2.1; also elsewhere on the board
+5V: C14.A (+), C15.P$1 (1), C19.P$1 (1), R7.2, U3.1 (IN), U4.1 (IN), U4.3 (EN); also elsewhere on the board
GND: C14.K (-), C15.P$2 (2), C16.P$2 (2), C17.P$2 (2), C18.P$2 (2), C19.P$2 (2), C20.P$2 (2), C21.P$2 (2), U3.2 (GND), U4.2 (GND); also elsewhere on the board
unnamed: C17.P$1 (1), C18.P$1 (1), SJ1.2, TP3.1, U3.5 (OUT)
unnamed: C16.P$1 (1), R7.1, U3.3 (EN)
unnamed: C20.P$1 (1), C21.P$1 (1), SJ2.2, U4.5 (OUT)

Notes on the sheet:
If the VDD and VDDA pins are split, the designer must ensure that VDDA power is applied before or simultaneously with VDD
FUENTE DE ALIMENTACIÓN PARA MCU (DOMINIO DIGITAL)
FUENTE DE ALIMENTACIÓN PARA MCU (DOMINIO ANALÓGICO)

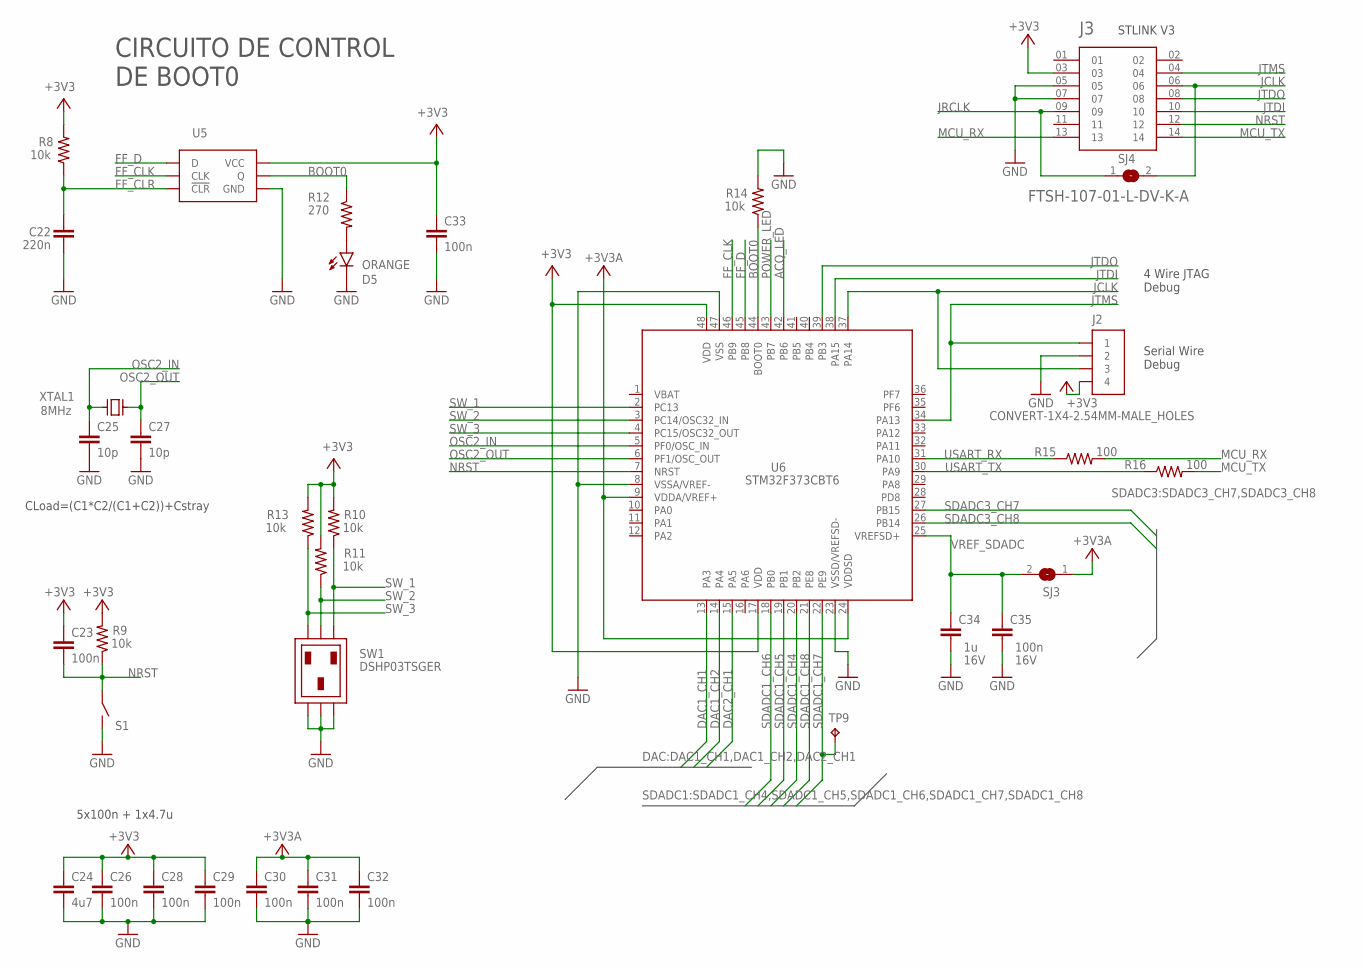
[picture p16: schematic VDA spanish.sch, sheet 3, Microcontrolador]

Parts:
C22: 220n; C_0603
C23, C26, C28, C29, C30, C31, C32, C33, C35: 100n; C_0603
C24: 4u7; C_0805
C25, C27: 10p; C_0603
C34: 1u; C_0603
D5: ORANGE; LED_0603_ARROW
J2: CONVERT-1X4-2.54MM-MALE_HOLES; 1X04
J3: FTSH-107-01-L-DV-K-A; SAMTEC_FTSH-107-01-L-DV-K-A
R8, R9, R10, R11, R13, R14: 10k; R_0603
R12: 270; R_0603
R15, R16: 100; R_0603
S1: TSWITCH_SMTR2; SMTR2
SJ3, SJ4: SJ
SW1: DSHP03TSGER; DIPSW-3
TP9: TPTP16R; TP16R
U5: SN74LVC1G175; SOT-23-6
U6: STM32F373CBT6; QFP50P900X900X160-48N
XTAL1: 8MHz; XTAL3.2X2.5; MPN 830108313809

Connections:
+3V3: C23.P$1 (1), C24.P$1 (1), C26.P$1 (1), C28.P$1 (1), C29.P$1 (1), C33.P$1 (1), J2.4, J3.03, R8.2, R9.2, R10.2, R11.2, R13.2, U5.5 (VCC), U6.17 (VDD), U6.48 (VDD); also elsewhere on the board
+3V3A: C30.P$1 (1), C31.P$1 (1), C32.P$1 (1), SJ3.1, U6.9 (VDDA/VREF+), U6.24 (VDDSD); also elsewhere on the board
ACQ_LED: U6.42 (PB6); also elsewhere on the board
BOOT0: R12.1, R14.1, U5.4 (Q), U6.44 (BOOT0); also elsewhere on the board
DAC1_CH1: U6.13 (PA3); also elsewhere on the board
DAC1_CH2: U6.14 (PA4); also elsewhere on the board
DAC2_CH1: U6.15 (PA5); also elsewhere on the board
FF_CLK: U5.1 (CLK), U6.46 (PB9)
FF_CLR: C22.P$1 (1), R8.1, U5.6 (!CLR!)
FF_D: U5.3 (D), U6.45 (PB8)
GND: C22.P$2 (2), C24.P$2 (2), C25.P$2 (2), C26.P$2 (2), C27.P$2 (2), C28.P$2 (2), C29.P$2 (2), C30.P$2 (2), C31.P$2 (2), C32.P$2 (2), C33.P$2 (2), C34.P$2 (2), C35.P$2 (2), D5.K, J2.2, J3.05, J3.07, R14.2, S1.P$3, S1.P$4, SW1.P$2, SW1.P$4, SW1.P$6, U5.2 (GND), U6.8 (VSSA/VREF-), U6.23 (VSSD/VREFSD-), U6.47 (VSS); also elsewhere on the board
JCLK: J2.3, J3.06, SJ4.2, U6.37 (PA14)
JRCLK: J3.09, SJ4.1
JTDI: J3.10, U6.38 (PA15)
JTDO: J3.08, U6.39 (PB3)
JTMS: J2.1, J3.04, U6.34 (PA13)
MCU_RX: J3.13, R15.2
MCU_TX: J3.14, R16.2
unnamed: D5.A, R12.2
NRST: C23.P$2 (2), J3.12, R9.1, S1.P$1, S1.P$2, U6.7 (NRST)
OSC2_IN: C25.P$1 (1), U6.5 (PF0/OSC_IN), XTAL1.P$3 (X2)
OSC2_OUT: C27.P$1 (1), U6.6 (PF1/OSC_OUT), XTAL1.P$1 (X1)
POWER_LED: U6.43 (PB7); also elsewhere on the board
SDADC1_CH4: U6.20 (PB2); also elsewhere on the board
SDADC1_CH5: U6.19 (PB1); also elsewhere on the board
SDADC1_CH6: U6.18 (PB0); also elsewhere on the board
SDADC1_CH7: TP9.TP, U6.22 (PE9)
SDADC1_CH8: U6.21 (PE8); also elsewhere on the board
SDADC3_CH7: U6.27 (PB15); also elsewhere on the board
SDADC3_CH8: U6.26 (PB14); also elsewhere on the board
SW_1: R10.1, SW1.P$1, U6.2 (PC13)
SW_2: R11.1, SW1.P$3, U6.3 (PC14/OSC32_IN)
SW_3: R13.1, SW1.P$5, U6.4 (PC15/OSC32_OUT)
USART_RX: R15.1, U6.31 (PA10); also elsewhere on the board
USART_TX: R16.1, U6.30 (PA9); also elsewhere on the board
VBAT: U6.1 (VBAT)
VREF_SDADC: C34.P$1 (1), C35.P$1 (1), SJ3.2, U6.25 (VREFSD+)

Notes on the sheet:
STLINK V3
5x100n + 1x4.7u
CLoad=(C1*C2/(C1+C2))+Cstray
CIRCUITO DE CONTROL DE BOOT0
Serial Wire Debug
4 Wire JTAG Debug

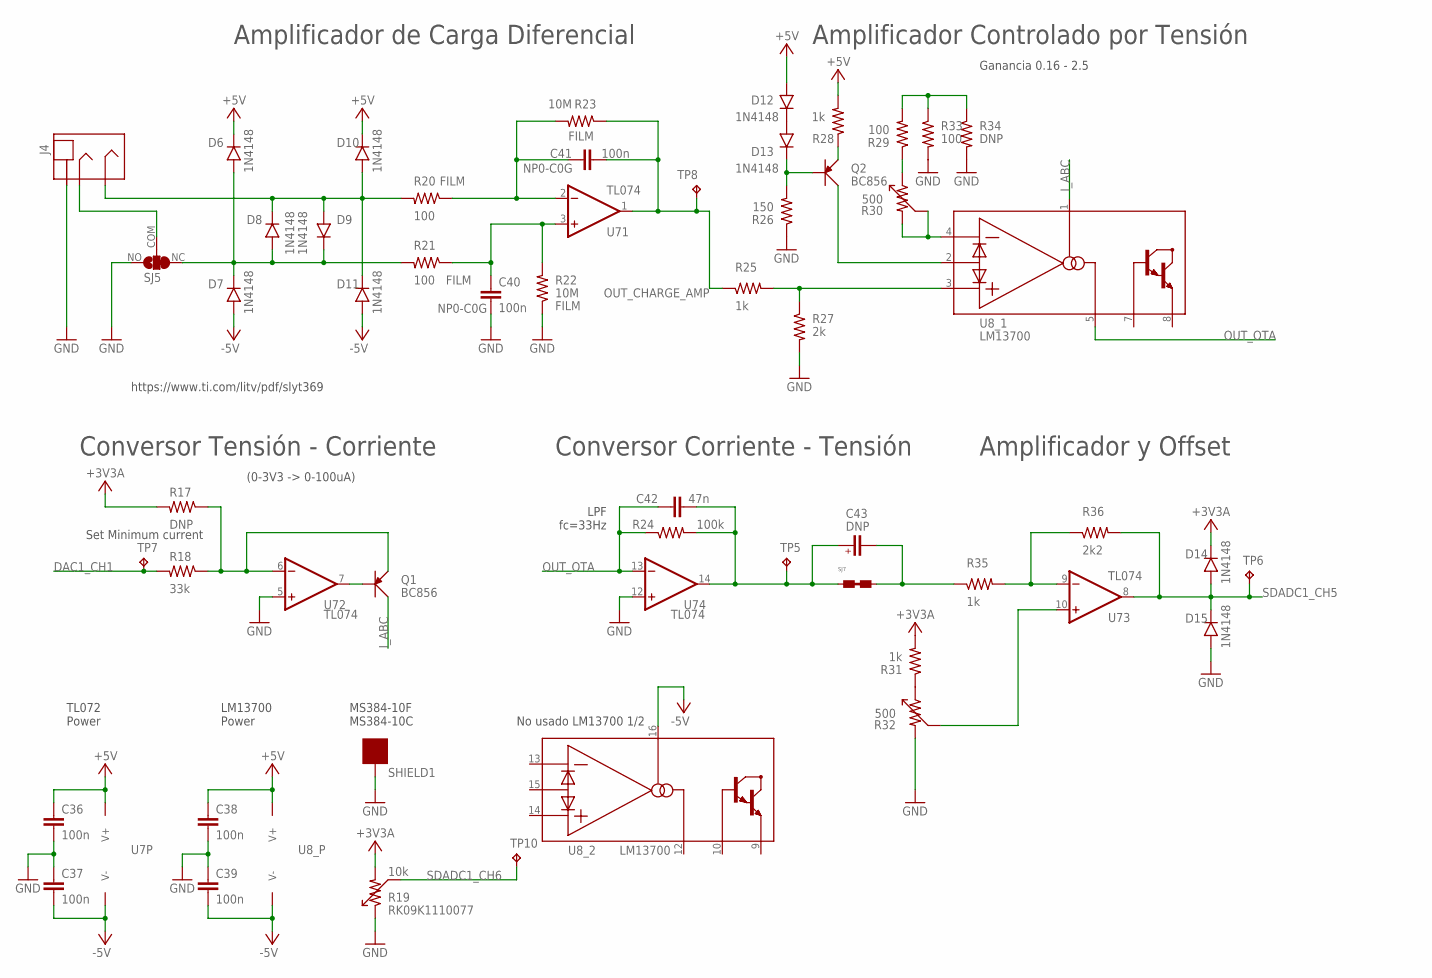
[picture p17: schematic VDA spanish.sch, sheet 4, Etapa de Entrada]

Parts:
C36, C37, C38, C39: 100n; C_0603
C40, C41: 100n; C_1206
C42: 47n; C_0603
C43: DNP; CAPAE830X680N
D6, D7, D8, D9, D10, D11, D12, D13, D14, D15: 1N4148; SOD123W
J4: STEREO-JACK; PJ-3200
Q1, Q2: BC856; SOT-23
R17, R34: DNP; R_0603
R18: 33k; R_0603
R19: 10k; POT-09VR1M; MPN RK09K1110077
R20, R21, R29, R33: 100; R_0603
R22, R23: 10M; R_0603
R24: 100k; R_0603
R25, R28, R31, R35: 1k; R_0603
R26: 150; R_0603
R27: 2k; R_0603
R30, R32: 500; RV3.2X4; MPN 3224W-1-501E
R36: 2k2; R_0603
SHIELD1: MS384
SJ5: SJ-PSS; SJ_2S
SJ7: SJUMPER-NC; SJ1
TP5, TP6, TP7, TP8, TP10: TPTP16R; TP16R
U7: TL074; SOIC127P600X175-14N
U8: LM13700; SO16

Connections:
+3V3A: D14.C (K), R17.2, R19.P$3 (2), R31.2; also elsewhere on the board
+5V: C36.P$1 (1), C38.P$1 (1), D6.C (K), D10.C (K), D12.A, R28.2, U7.4 (V+), U8.11 (V+); also elsewhere on the board
-5V: C37.P$2 (2), C39.P$2 (2), D7.A, D11.A, U7.11 (V-), U8.6 (V-), U8.16 (AMP_BIAS); also elsewhere on the board
DAC1_CH1: R18.2, TP7.TP; also elsewhere on the board
GND: C36.P$2 (2), C37.P$1 (1), C38.P$2 (2), C39.P$1 (1), C40.P$2 (2), D15.A, J4.1 (SLEEVE), R19.P$1 (1), R22.1, R26.1, R27.2, R32.3 (2), R33.2, R34.2, SHIELD1.P$1, SHIELD1.P$2, SJ5.NO, U7.5 (+IN), U7.12 (+IN); also elsewhere on the board
I_ABC: Q1.3 (C), U8.1 (AMP_BIAS)
unnamed: C42.P$1 (1), C43.1 (+), R24.2, SJ7.P$1, TP5.TP, U7.14 (OUT)
unnamed: C40.P$1 (1), R21.1, R22.2, U7.3 (+IN)
unnamed: C41.P$1 (1), R20.1, R23.2, U7.2 (-IN)
unnamed: C43.2 (-), R35.1, SJ7.P$2
unnamed: J4.3 (RING), SJ5.COM
unnamed: Q1.2 (E), R17.1, R18.1, U7.6 (-IN)
unnamed: R29.2, R33.1, R34.1
unnamed: Q1.1 (B), U7.7 (OUT)
unnamed: Q2.2 (E), R28.1
unnamed: D12.C (K), D13.A
unnamed: R31.1, R32.1
unnamed: D8.C (K), D9.A, D10.A, D11.C (K), J4.2 (TIP), R20.2
unnamed: D6.A, D7.C (K), D8.A, D9.C (K), R21.2, SJ5.NC
unnamed: R32.2 (C), U7.10 (+IN)
unnamed: R25.2, R27.1, U8.3 (+)
unnamed: R30.2 (C), R30.3 (2), U8.4 (-)
unnamed: Q2.3 (C), U8.2 (D_BIAS)
unnamed: R29.1, R30.1
unnamed: D13.C (K), Q2.1 (B), R26.2
unnamed: R35.2, R36.1, U7.9 (-IN)
OUT_CHARGE_AMP: C41.P$2 (2), R23.1, R25.1, TP8.TP, U7.1 (OUT)
OUT_OTA: C42.P$2 (2), R24.1, U7.13 (-IN), U8.5 (OUT)
SDADC1_CH5: D14.A, D15.C (K), R36.2, TP6.TP, U7.8 (OUT); also elsewhere on the board
SDADC1_CH6: R19.P$2 (C), TP10.TP; also elsewhere on the board

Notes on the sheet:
TL072 Power
LM13700 Power
https://www.ti.com/litv/pdf/slyt369
MS384-10F MS384-10C
Amplificador de Carga Diferencial
Amplificador Controlado por Tensión
Conversor Tensión - Corriente
(0-3V3 -> 0-100uA)
No usado LM13700 1/2
Set Minimum current
Ganancia 0.16 - 2.5
LPF fc=33Hz
Conversor Corriente - Tensión
Amplificador y Offset

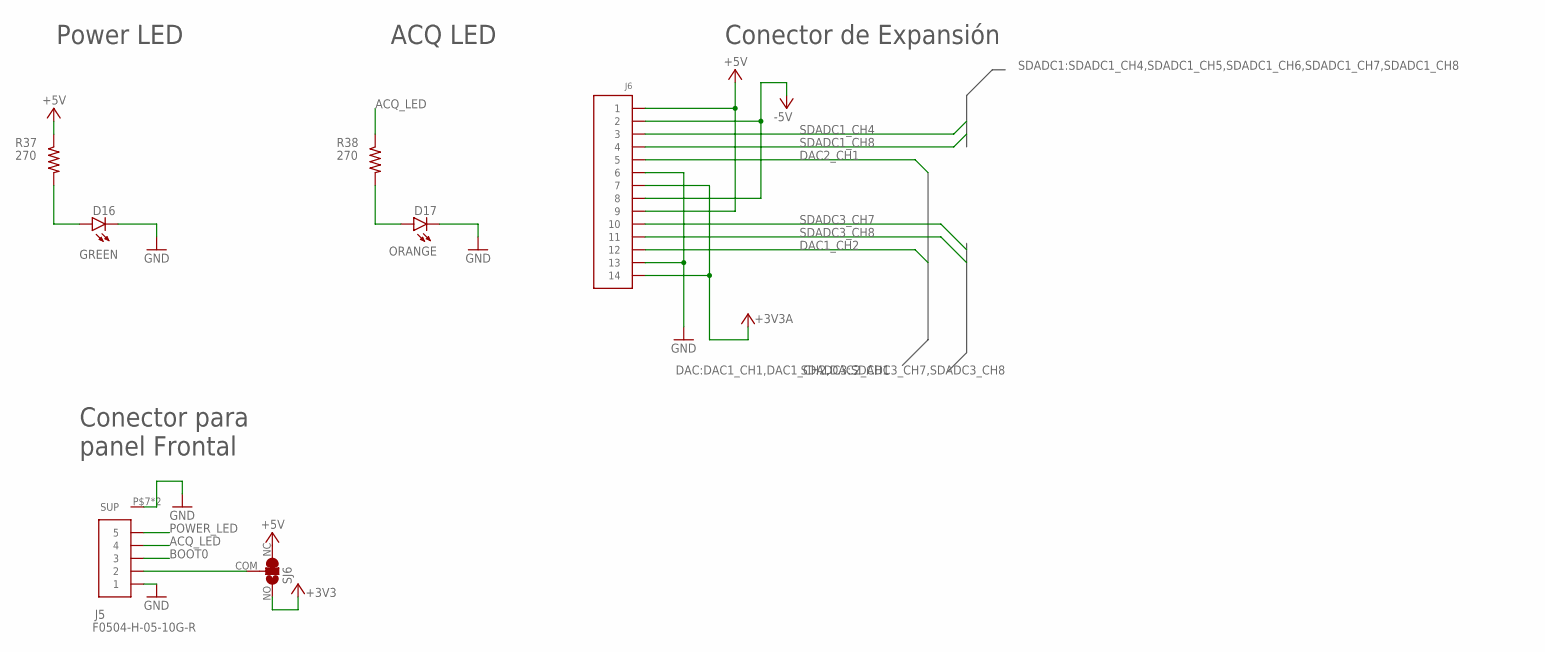
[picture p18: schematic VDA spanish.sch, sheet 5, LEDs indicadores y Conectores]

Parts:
D16: GREEN; LED_0603_ARROW
D17: ORANGE; LED_0603_ARROW
J5: F0504-H-05-10G-R
J6: CONVERT-2X7-2.54MM-FEMALE; CONN-VERT-2.54MM-2X7-FEMALE
R37, R38: 270; R_0603
SJ6: SJ-PSS; SJ_2S

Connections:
+3V3: SJ6.NO; also elsewhere on the board
+3V3A: J6.7, J6.14; also elsewhere on the board
+5V: J6.1, J6.9, R37.1, SJ6.NC; also elsewhere on the board
-5V: J6.2, J6.8; also elsewhere on the board
ACQ_LED: J5.P$4 (4), R38.1; also elsewhere on the board
BOOT0: J5.P$3 (3); also elsewhere on the board
DAC1_CH2: J6.12; also elsewhere on the board
DAC2_CH1: J6.5; also elsewhere on the board
GND: D16.K, D17.K, J5.P$1 (1), J5.P$7 (SUP), J5.P$8 (SUP), J6.6, J6.13; also elsewhere on the board
unnamed: D17.A, R38.2
unnamed: D16.A, R37.2
unnamed: J5.P$2 (2), SJ6.COM
POWER_LED: J5.P$5 (5); also elsewhere on the board
SDADC1_CH4: J6.3; also elsewhere on the board
SDADC1_CH8: J6.4; also elsewhere on the board
SDADC3_CH7: J6.10; also elsewhere on the board
SDADC3_CH8: J6.11; also elsewhere on the board

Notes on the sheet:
Power LED
ACQ LED
Conector de Expansión
Conector para panel Frontal

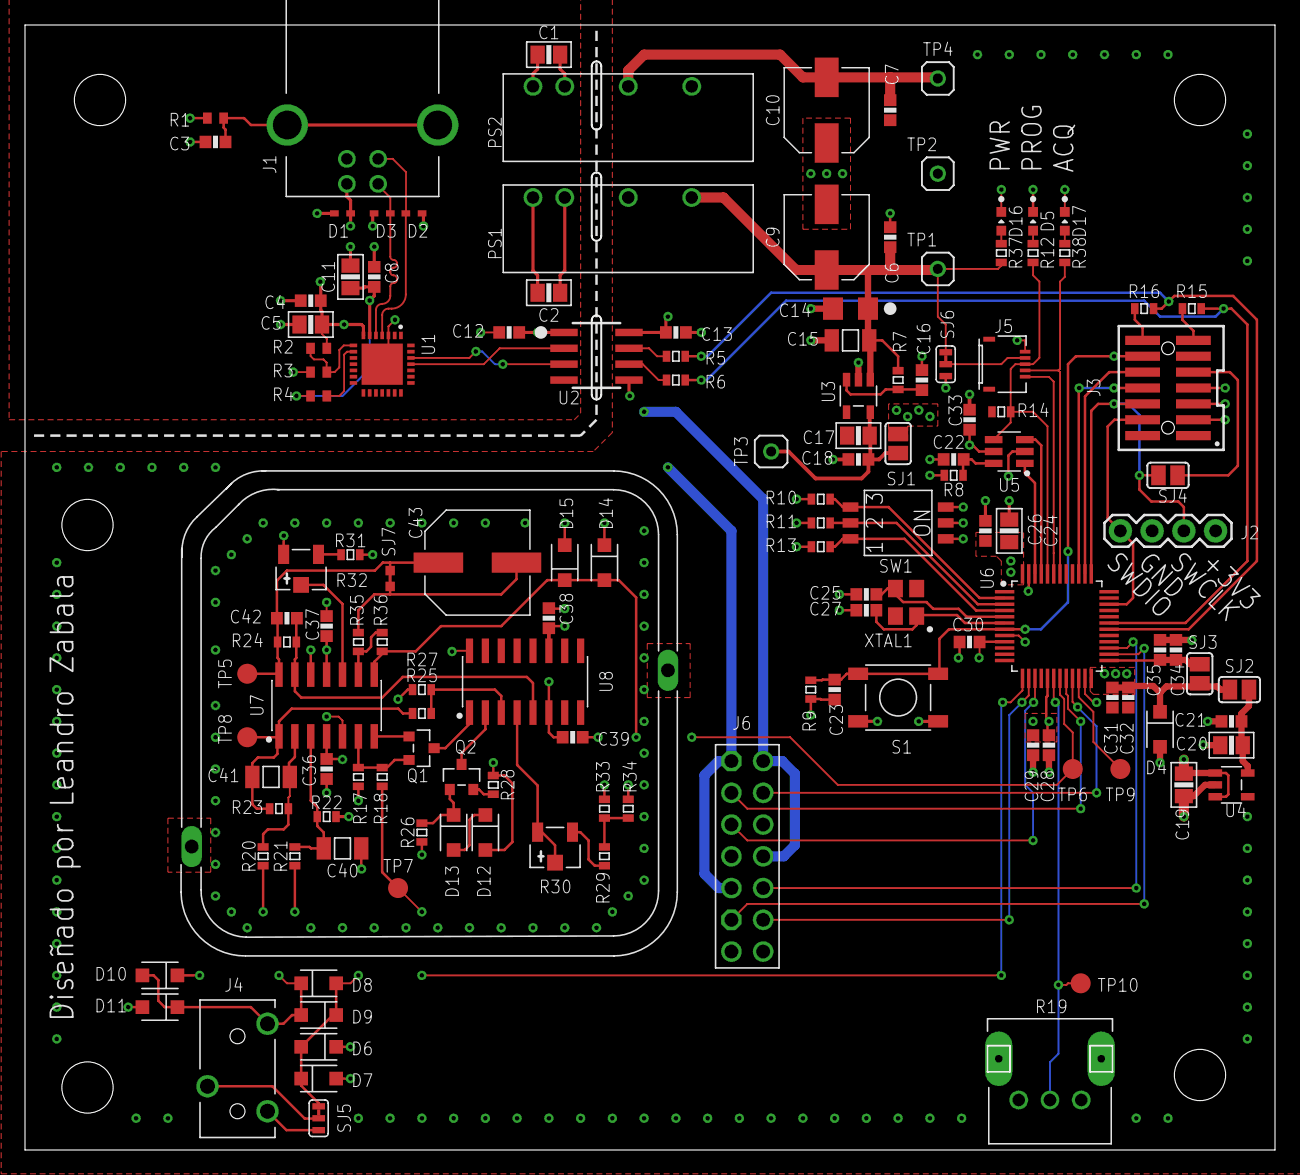
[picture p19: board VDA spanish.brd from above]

Board: 4 copper layers, 100.0 x 90.0 mm, 137 parts (0 on the bottom side), 79 nets.

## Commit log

2024-12-29 starting layout
    [VDA.brd, VDA.sch]
2025-01-01 inicio layout
    [VDA.brd, VDA.sch]
2025-01-03 trabajando en el layout
    [VDA.brd, VDA.sch]
2025-01-06 panel frontal y posterior listos
    [Panel Frontal.brd, Panel Frontal.sch, Panel Posterior.brd, Panel Posterior.sch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]
2025-01-17 layout avanzado
    [Panel Frontal.sch, Panel Posterior.brd, Panel Posterior.sch, VDA.brd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]
2025-01-19 cambio de conector para expansion
    [VDA.brd, VDA.sch]
2025-01-19 layout terminado
    [VDA.brd, VDA.sch]
2025-01-20 trabajando en los panelizados
    [Panel Frontal.brd, Panel Posterior.sch, Panelizado_completo.brd, Panelizado_completo.sch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]
2025-01-20 invertí todo el panel frontal para disminuir costo de ensamblaje
    [Panel Frontal.brd]
2025-01-22 BOM del adquisidor listo
    [BOM-Panelizado_frentes_PCBWAY.xlsx, Panelizado_frentes.brd, Panelizado_frentes.csv, Panelizado_frentes.sch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]
2025-01-22 retoques en capa tnames del adquisidor
    [VDA.brd, VDA.sch]
2025-01-22 archivos listos para pcbway
    [BOM_VDA_PCBWAY.xlsx, PnP_VDA_front.csv, PnP_VDA_front_PCBWAY.csv, VDA.csv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]
2025-05-01 Archivos mas ordenados
    [BOM-Panelizado_frentes_PCBWAY.xlsx, Panel Frontal.brd, Panel Frontal.sch, Panel Posterior.brd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]
2025-06-08 added README file
    [Panel Frontal.sch, VDA.sch]
2025-06-08 readme completo cambio de fotos
2025-06-08 readme completo cambio de fotos1
2025-06-08 readme completo cambio de fotos2
